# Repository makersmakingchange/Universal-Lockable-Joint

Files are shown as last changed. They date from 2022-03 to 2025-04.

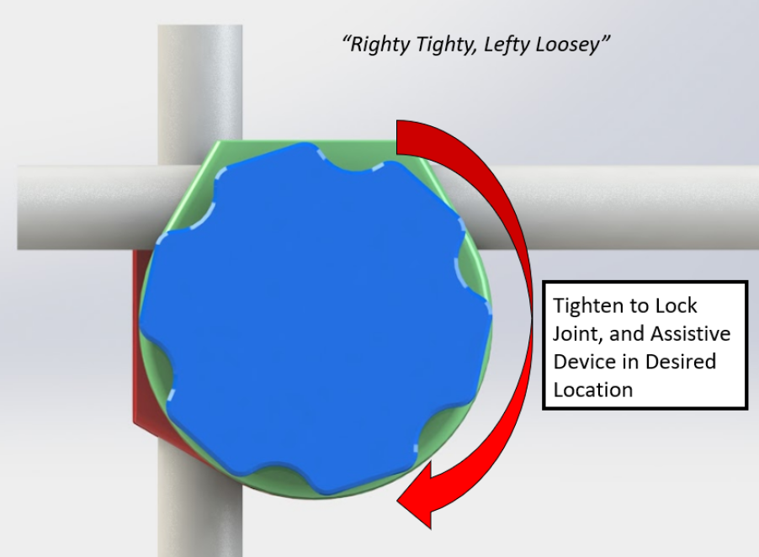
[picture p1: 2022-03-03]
Photos/adjustment.png

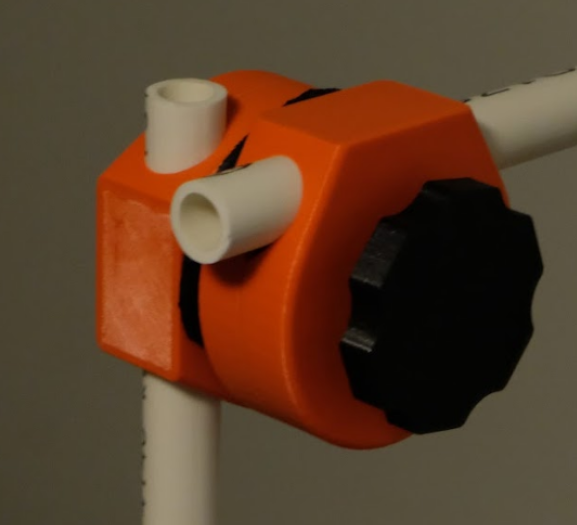
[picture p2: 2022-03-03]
Photos/Joint_orange.png

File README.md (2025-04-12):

# Universal Lockable Joint

## Overview

This is a low-cost 3D printable joint to be used for mounting assistive technology devices. The joint allows for 1/2 inch PVC pipes to be inserted in and allow movement in all degrees of freedom. This device is intended to work with other [PVC Accessible Mounting System (PAMS)](https://github.com/makersmakingchange/PVC-Accessible-Mounting-System) mounting devices to allow adjustable and lockable positioning in all directions.

Picture of 3D printed Universal Loackable Joint with PVC pipe.

The PVC is placed into the lockable joint and then positioned in the desired location. Once the optimal mounting location is found the joint can be locked in place by turning the handle of the device. This locks all the directions of the device. This can be repositioned by simply loosening the handle and tightening once again.

Picture showing how to adjust the joint. The knob is turned clockwise to tighten and counterclockwise to loosen.

**More info at:**
- https://makersmakingchange.com/project/universal-lockable-joint/

## Versions/Customization
There is an optional larger handle that can be 3D printed as well. This version is better for individuals with reduced grip strength and allows more area to grab onto. If you are building this device for a request, ask the user if they want to try out the larger handle. The STL can be found in the "3D Print Files" folder above.

## Build Instructions

Build instructions and design files are available in this repository. The instructions and guides can be found under "Documentation". The STLs can be found under "3D Print Files". The solid model files (STEP) can be found in "Design Files". Photos of the device can be seen under "Photos".

### Skills Required
- Fine motor skills 
- Twisting bolt into place (Gripping) 
- Using tools

### Tools
- Mallet/Hammer (optional)

### Components
- 1x - M10 x 70 Hex Bolt  - Link
- 1x - M10 Hex Nut - Link
- 1x - M10 Flat Washer - Link
- 1x - Rubber Washer - Link

### 3D Printing
All Components can be printed with no support at 20% infill with a 0.2 layer height.
- 1x - Joint Handle
- 1x - Left half of shell housing
- 1x - Right half of shell housing

## Attribution
University of Alberta Capstone Team:
- Matthew Brydges
- Bobby Li
- Stanley Lim
- Miguel Oliveira
- Marco Villegas

<!-- ABOUT MMC START -->
## About Makers Making Change
[Makers Making Change Logo](https://www.makersmakingchange.com/)

Makers Making Change is a program of [Neil Squire](https://www.neilsquire.ca/), a Canadian non-profit that uses technology, knowledge, and passion to empower people with disabilities.

Makers Making Change leverages the capacity of community based Makers, Disability Professionals and Volunteers to develop and deliver affordable Open Source Assistive Technologies.

 - Website: [www.MakersMakingChange.com](https://www.makersmakingchange.com/)
 - GitHub: [makersmakingchange](https://github.com/makersmakingchange)
 - Bluesky: [@makersmakingchange.bsky.social](https://bsky.app/profile/makersmakingchange.bsky.social)
 - Instagram: [@makersmakingchange](https://www.instagram.com/makersmakingchange)
 - Facebook: [makersmakechange](https://www.facebook.com/makersmakechange)
 - LinkedIn: [Neil Squire Society](https://www.linkedin.com/company/neil-squire-society/)
 - Thingiverse: [makersmakingchange](https://www.thingiverse.com/makersmakingchange/about)
 - Printables: [MakersMakingChange](https://www.printables.com/@MakersMakingChange)

### Contact Us
For technical questions, to get involved, or to share your experience we encourage you to [visit our website](https://www.makersmakingchange.com/) or [contact us](https://www.makersmakingchange.com/s/contact).
<!-- ABOUT MMC END -->
 - [GitHub](https://github.com/makersmakingchange)
 - [Thingiverse](https://www.thingiverse.com/makersmakingchange/about)
 - Twitter: [@makermakechange](https://twitter.com/makermakechange)
 - Instagram: [@makersmakingchange](https://www.instagram.com/makersmakingchange)

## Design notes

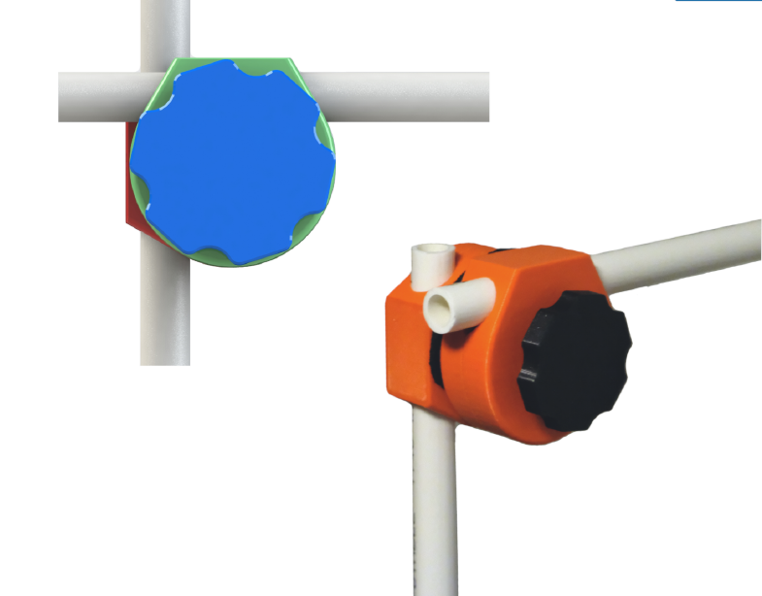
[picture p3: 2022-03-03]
Photos/bothsides.png

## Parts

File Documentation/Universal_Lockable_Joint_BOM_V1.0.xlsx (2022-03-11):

Device: Universal Lockable Joint (Metric) |  | Total Cost | Total Print time (hr) | Total filament (g)
Version: V1.0 | Date Created: 11/26/2021 | $9.37 | 20.27 | 223.1
Commercial Parts:
Part type (Electrical. Mechanical, Sanitization, ect) | Part Name | Quantity Needed | Pkg Quantity | Price per package | Price per Unit | Price for qty needed | Link
Mechanical | M10x70 Hex Bolt | 1 | 1 | $2.03 | $2.03 | $2.03 | https://www.homedepot.ca/product/paulin-m10-1-50-x-70mm-class-8-8-metric-hex-cap-screw-din-931-zinc-plated/1000122780
Mechanical | M10 Hex Nut | 1 | 1 | $0.37 | $0.37 | $0.37 | https://www.homedepot.ca/product/paulin-m10-1-50-class-8-metric-hex-nut-din-934-zinc-plated/1000128523
Mechanical | Rubber Washer | 1 | 1 | $1.20 | $1.20 | $1.20 | https://www.homedepot.ca/product/paulin-3-8-id-2-od-inch-rubber-washer-1-16-inchthick-/1000144042
Mechanical | M10 Flat Washer | 1 | 1 | $0.19 | $0.19 | $0.19 | https://www.homedepot.ca/product/paulin-m10-metric-flat-washers-zinc-plated-iso-7089/1000128559
3D Printed Parts ESTIMATED PRICING USING 1KG ROLL COST: | $25.00
Part | Description | Quantity Needed | TOTAL Mass (g) | Estimated Price | Print Time (Min) | Link
Left Side | Clam-Shell left side, with indent for bolt | 1 | 103.53 | $2.59 | 564
Right Side | Clam-Shell right side | 1 | 103.48 | $2.59 | 559
Handle | Handle with indent for nut | 1 | 16.09 | $0.40 | 93
 |  |  |  | $0.00
 |  |  |  | $0.00
 |  |  | Total Print Cost: | $5.58
Tools for Assembly
Hammer or Mallet (optional)
Alternatives (if there are other sources for some parts link them below)
Part and description | Link

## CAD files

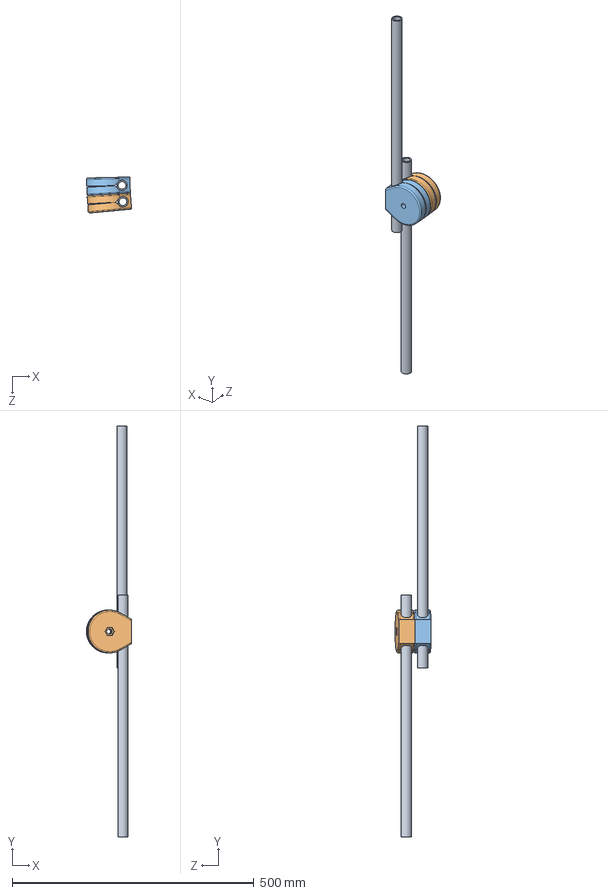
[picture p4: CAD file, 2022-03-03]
Design Files/clamshell3.SLDASM
93.6 x 850.0 x 74.6 mm
pvc x 2
shell_left
shell_right

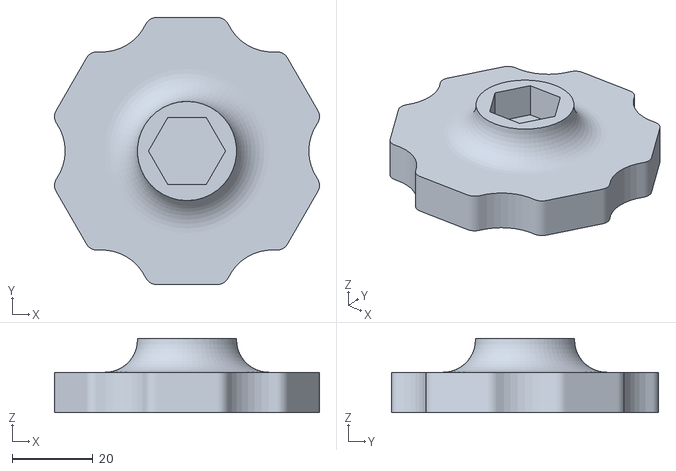
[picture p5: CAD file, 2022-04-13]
3D Print Files/handle.STL
65.5 x 66.0 x 18.4

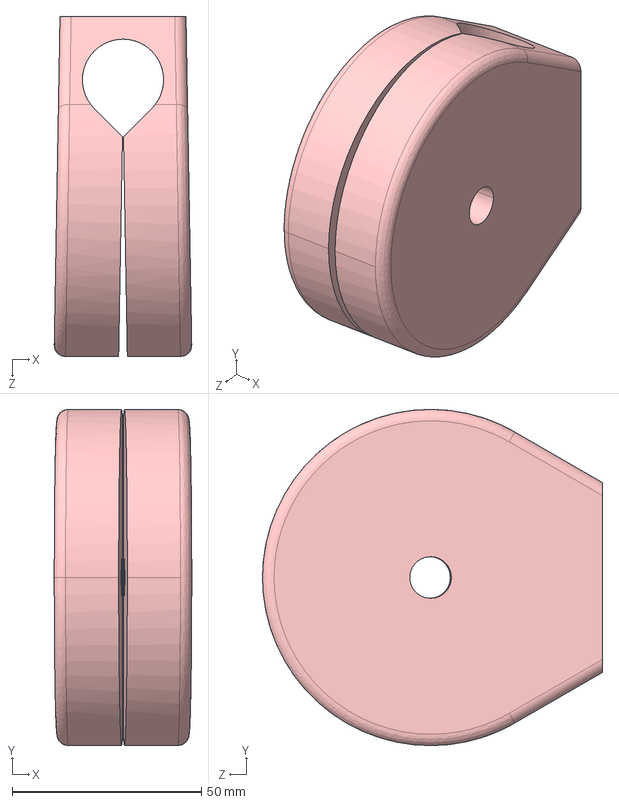
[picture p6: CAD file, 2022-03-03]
Design Files/shell_right.STEP
36.4 x 88.9 x 89.9 mm

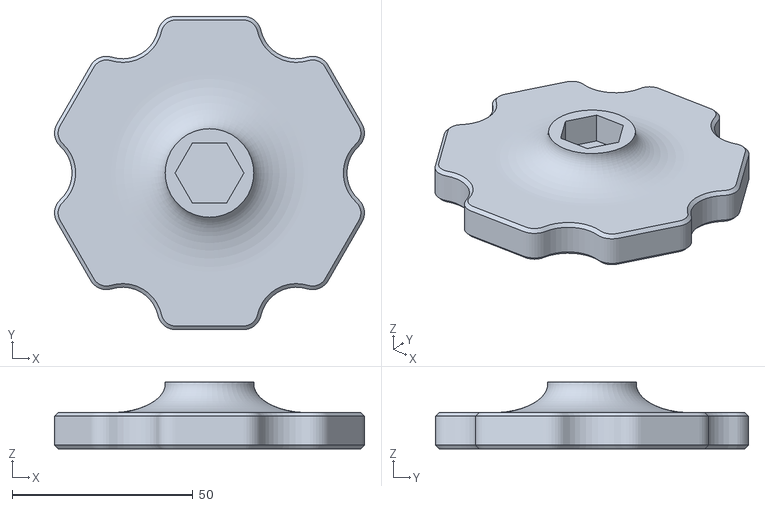
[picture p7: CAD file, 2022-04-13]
3D Print Files/large_handle.STL
85.7 x 86.6 x 18.4

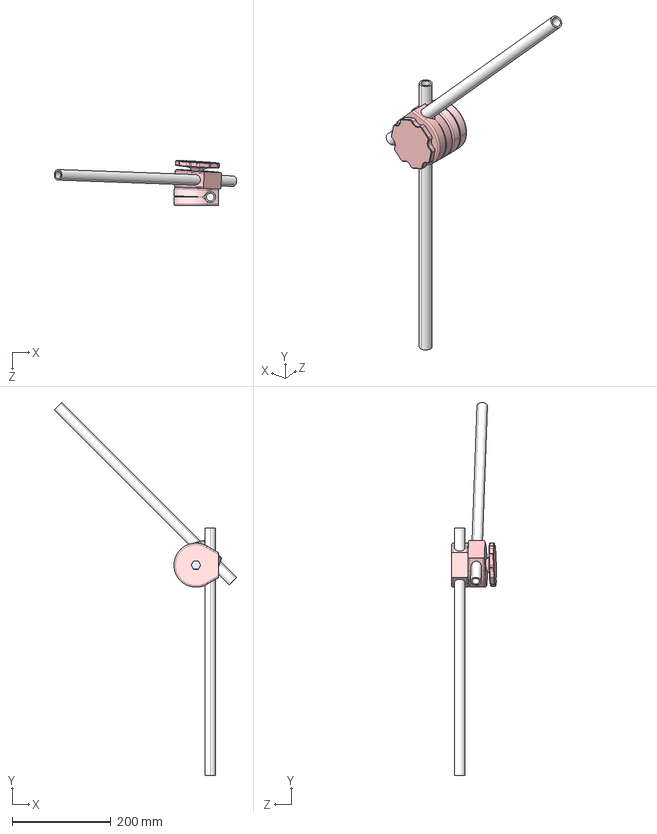
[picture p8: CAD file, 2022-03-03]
Design Files/clamshell_45.STEP
368.4 x 753.6 x 91.1 mm
pvc x 2
shell_left
shell_right
handle
bolt

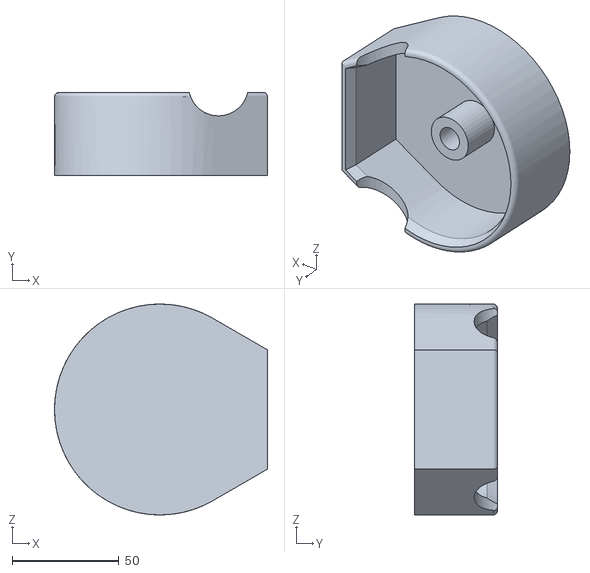
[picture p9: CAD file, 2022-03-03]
3D Print Files/bolt_cover.STL
99.9 x 39.0 x 98.9

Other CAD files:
3D Print Files/right_side.STL
Design Files/shell_left.STEP
3D Print Files/left_side.STL
Design Files/clamshell_0.STEP
Design Files/shell_left.SLDPRT
Design Files/shell_right.SLDPRT

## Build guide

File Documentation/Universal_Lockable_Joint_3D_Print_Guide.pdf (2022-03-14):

V5.00 | December 2021

## Universal Lockable Joint

## 3D PRINTING GUIDE

© 2021 by Matthew Brydges, Miguel Oliveira, Marco Villegas, Stanley Lim, Bobby Li. This work is licensed under the CC BY SA 4.0 License: http://creativecommons.org/licenses/by-sa/4.0

### 3D Printing Summary

Metrics | Metric Standard | Imperial Standard
Total Print Time (min) | 1110 | 1110
Total Number of Components | 3 | 3
Typical Total Mass (g) | 619 | 619
Typical Number of Print Setups | 1 | 1
3D Printing Settings Required | Print File Name | Qty | Total Print Time (hr:min) | Mass (g) | Infill (%) | Support (Y/N) | Layer Height/ Nozzle Diameter (mm) | Notes (orientation, special settings, etc)
| Left_Side.stl | 1 | 8:30 | 30 | 20 | N | 0.2 | -Recommend 4 or 5 shells/perimeters. - Print “standing”, as seen in pictures below.
| Right_Side.stl | 1 | 8:30 | 30 | 20 | N | 0.2 | -Same notes as “Left Side” above.
| Handle.stl | 1 | 1:30 | 18 | 20 | N | 0.2 | -Print with flat face on print bed, as seen in picture.
| Large_Handle.stl | - | 2:00 | 22 | 20 | N | 0.2 | -This is an alternate design to the Hande
| Bolt_Cover | - | 6:02 | 60 | 20 | N | 0.2 | -Only required if the bolt is longer than intended and is sticking out

Optional

### Post-Processing

- Light sanding might be necessary to correct any sharp edges.

### Customization Options

- PETG recommended, PLA works well.
- Color of print is up to personal preference.
- Ensure that correct configuration is used based on fasteners purchased, if M10 bolt and nut use metric, if 3/8” nut and bolt use imperial.

## 3D PRINTING GUIDE

### Examples of Quality Prints:

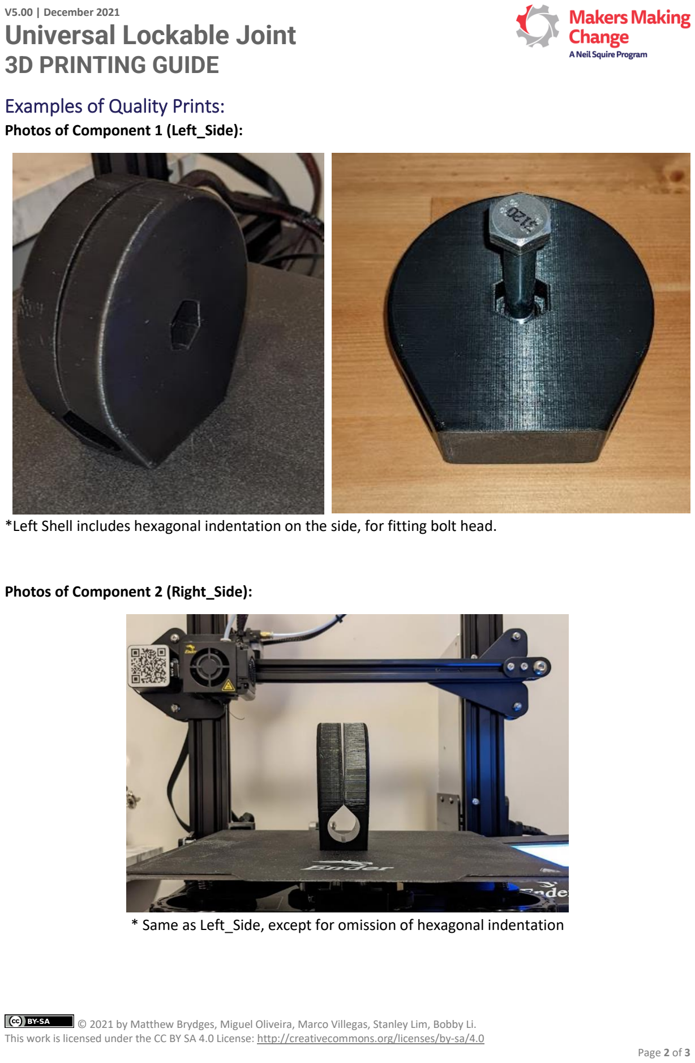
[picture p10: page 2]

Photos of Component 1 (Left_Side):

*Left Shell includes hexagonal indentation on the side, for fitting bolt head.

Photos of Component 2 (Right_Side):

* Same as Left_Side, except for omission of hexagonal indentation

## 3D PRINTING GUIDE

Photos of Component 3 (Handle):

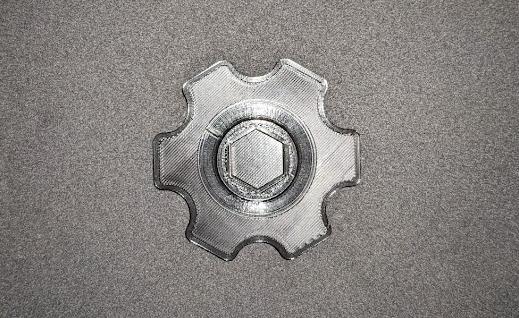
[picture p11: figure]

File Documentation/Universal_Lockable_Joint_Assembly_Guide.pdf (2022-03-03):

V5.00 | December 2021

# Universal Lockable Joint

# ASSEMBLY GUIDE

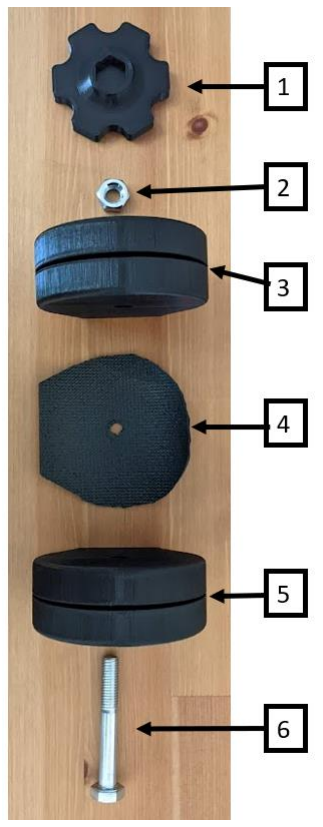
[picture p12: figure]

© 2021 by Matthew Brydges, Miguel Oliveira, Marco Villegas, Stanley Lim, Bobby Li. This work is licensed under the CC BY SA 4.0 License: http://creativecommons.org/licenses/by-sa/4.0

# Required Components

## BOM

## 1. Handle 2. M10 Nut 3. Left Side Shell 4. Rubber Gasket 5. Right Side Shell 6. M10 x 70 Bolt

## *Parts may slightly vary depending on metric or imperial configuration. Assembly is the same for

both.

# Required Tools

- No tools required for assembly.
- Hammer or mallet may be used to slide nut and bolt into friction fit.
- Glue may be used to secure nut and bolt in place.

# Required Personal Protective Equipment (PPE)

- No Personal Protective Equipment required.

# ASSEMBLY GUIDE

# Assembly Instructions

## Step 1

Refer to printing guide and print all components.

## Step 2

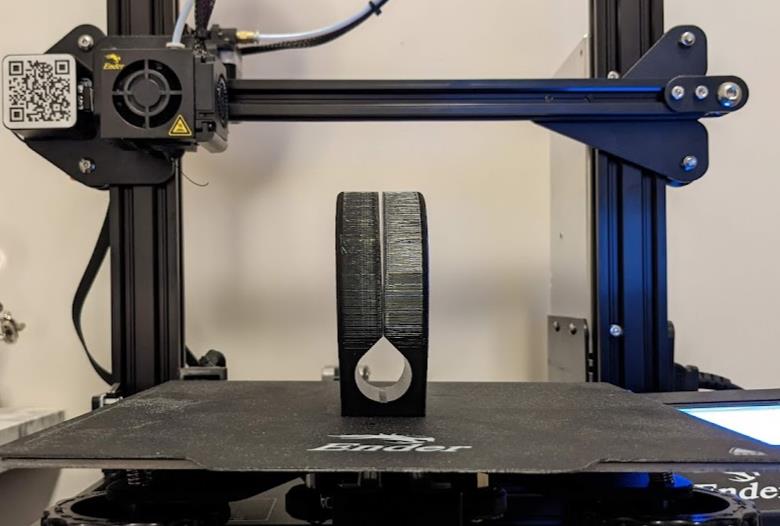
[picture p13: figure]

Slide bolt into place on right side shell (the shell with the hexagonal hole).

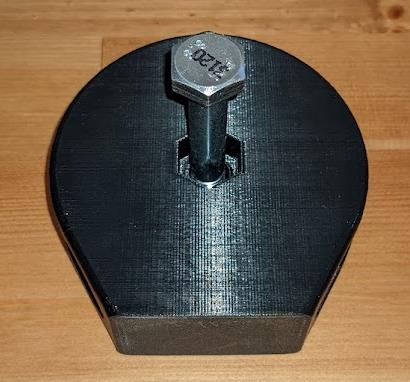
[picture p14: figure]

# ASSEMBLY GUIDE

## Step 3

Turn the assembly so that the head of the bolt is on a flat surface, and press down on the joint until the bolt is flush with the shell, alternatively a hammer or mallet may be used to get the bolt in place.

## Step 4

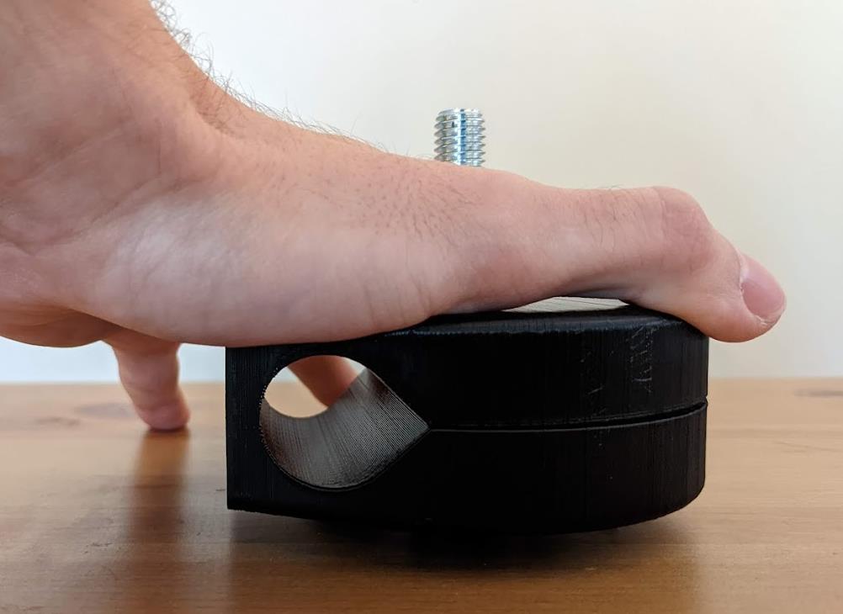
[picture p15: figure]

Place the rubber gasket on the bolt.

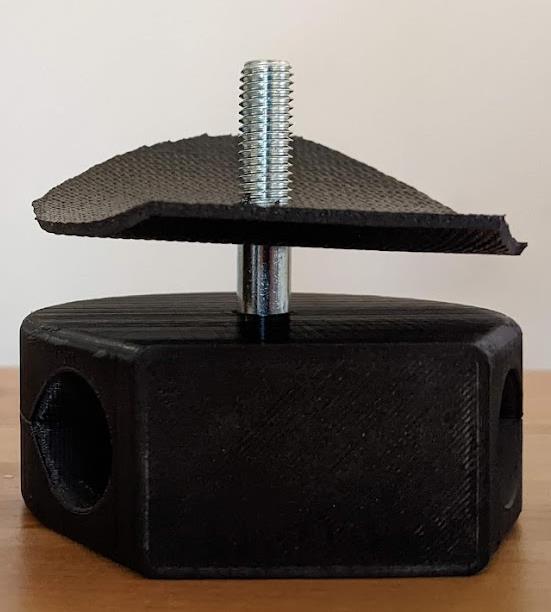
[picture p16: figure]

# ASSEMBLY GUIDE

## Step 5

Place the left shell on the bolt above the rubber gasket.

## Step 6

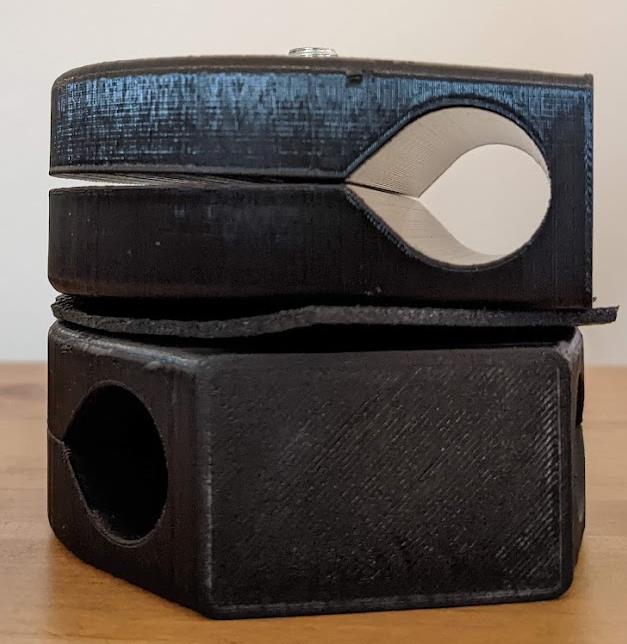
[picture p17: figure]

Place the nut at the end of the bolt, above the left shell.

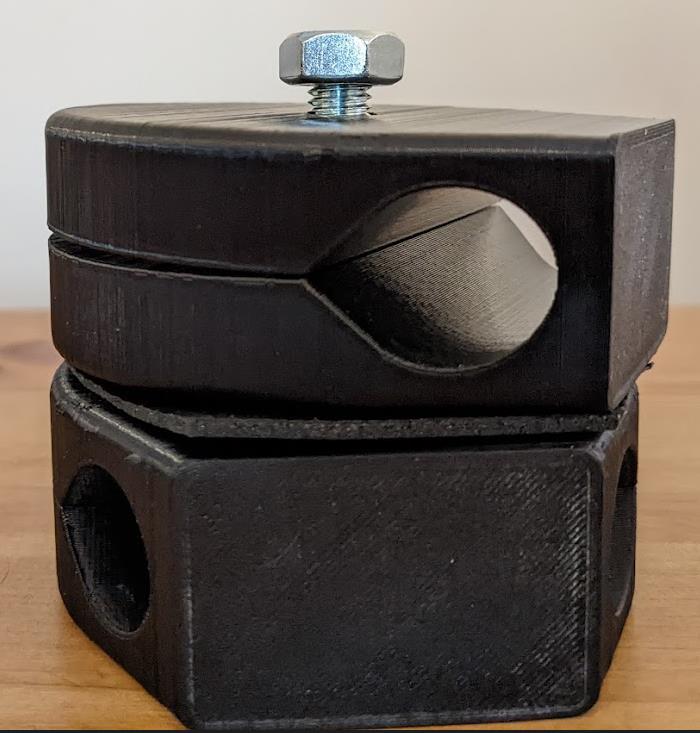
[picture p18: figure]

# ASSEMBLY GUIDE

## Step 7

Place the handle above the nut, and press down so that it slides in the friction fit.

## Step 4

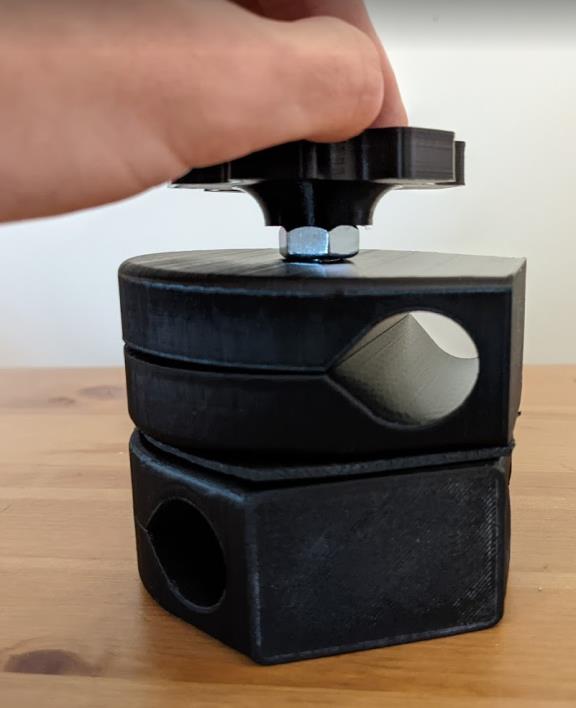
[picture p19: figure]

Congratulations! The joint is assembled! Now just slide the PVC in the slots to use with the PVC Assistive Mounting System (PAMS).

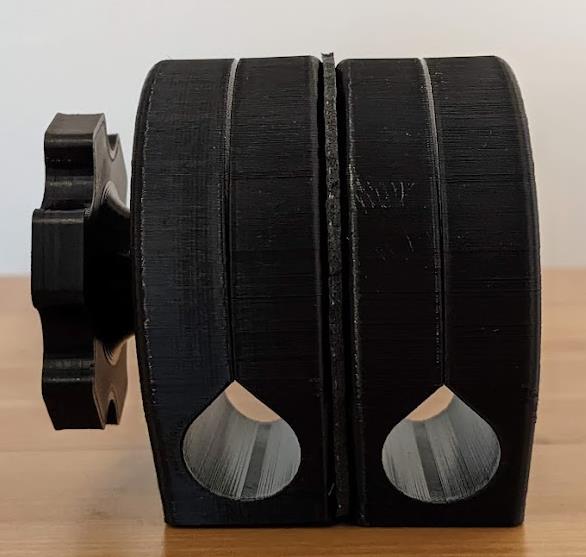
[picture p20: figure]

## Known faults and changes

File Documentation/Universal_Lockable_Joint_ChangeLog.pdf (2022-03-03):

V5.00 | December 2021

## Universal Lockable Joint

## CHANGELOG

© 2021 by Matthew Brydges, Miguel Oliveira, Marco Villegas, Stanley Lim, Bobby Li. This work is licensed under the CC BY SA 4.0 License: http://creativecommons.org/licenses/by-sa/4.0

## Version 1.0 | Date 10/05/2021

Basic concept is first generated. Features include:

- Clamshell design
- 3 3D-printed parts and 3 off-the-shelf components
- Easy to print and assemble
- Allows for placement of assistive device virtually anywhere

Cracked along PVC barrel under high loads

## Version 2.0 - 5.0 | Date 12/01/2021

- Increased tolerance for fasteners and PVC
- Angled Inner and outer faces by 2 degrees to increase contact area and avoid slipping
- Increased wall thickness to 6 mm

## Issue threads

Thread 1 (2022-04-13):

### ISSUE TITLE
handle.stl and large_handle.stl both contain other parts

### ISSUE THREAD

**Issue by Billfred** [makersmakingchange/Universal-Lockable-Joint#1]
https://github.com/makersmakingchange/Universal-Lockable-Joint/blob/main/3D%20Print%20Files/handle.STL and https://github.com/makersmakingchange/Universal-Lockable-Joint/blob/main/3D%20Print%20Files/large_handle.STL both appear to contain exports of _all_ the parts for this joint, not just the handles.  

Which makes it challenging to make everything fit neatly on the print bed. 😅

**Comment by jakemcivor** [comment]
Thanks - this was probably a result of me trying to correct the print orientations in the STLs.

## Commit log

2022-04-03 Correct orientation
    Rotated stls so they are in the intended print orientation.
    [handle.STL, large_handle.STL]
2022-04-03 Change filenames to match documentation
    [left_side.STL, right_side.STL]
2022-04-13 Fix STLs
    Fixes old STLs that had all parts inside and not just the handles.
    [handle.stl, large_handle.stl]
2022-04-13 Delete handle.stl
    oops
    [handle.stl]
2022-04-13 Delete large_handle.stl
    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
    [large_handle.stl]
2022-04-13 Fix STLs
    Previous versions had additional parts inside.
    [handle.STL, large_handle.STL]
